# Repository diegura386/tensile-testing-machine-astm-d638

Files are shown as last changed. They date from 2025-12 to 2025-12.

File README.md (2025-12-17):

# tensile-testing-machine-astm-d638
Open-hardware tensile testing machine for plastics (ASTM D638). Project by Diego Víctor Saavedra Ravier.  ➠  [Read this README in English](README.en.md)

# Máquina de Ensayo de Tracción de Plásticos (ASTM D638)



Máquina de ensayo de tracción (UTM) para **plásticos**, orientada a piezas fabricadas por **manufactura aditiva (impresión 3D)** y diseñada para cumplir con los requerimientos de la norma **ASTM D638**, para garantizar obtener ensayos válidos y comparables con otras máquinas bajo el mismo estándar.

Proyecto de **grado en Ingeniería Electromecánica** – UTN FR Chubut.

> Título académico: **Máquina de ensayo de tracción de plásticos** *Diseño y cálculo según norma ASTM D638*

> Autor: **Diego Víctor Saavedra Ravier** 

> Año: **2025**  

> Licencias: **CC BY-SA 4.0** (documentación) y **CERN-OHL-S v2** (hardware)

> Documentación completa del trabajo   ➠   

---

## 📸 Vista general de la máquina

<p align="center">
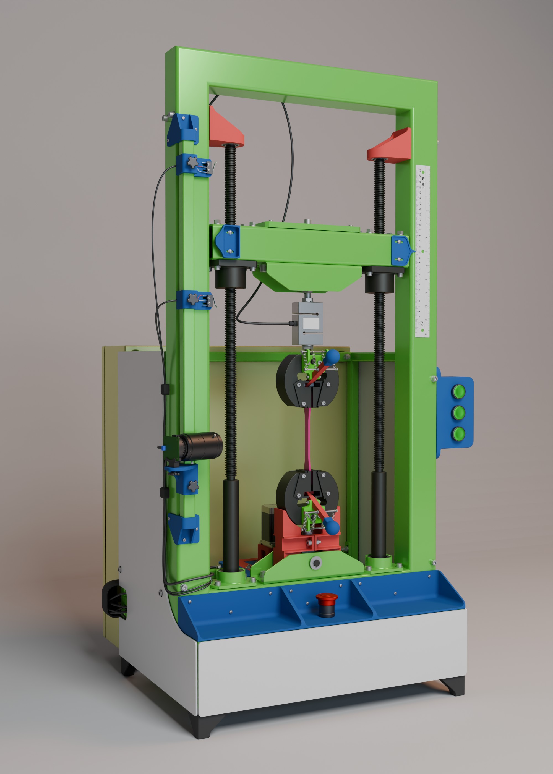
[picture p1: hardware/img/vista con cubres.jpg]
Máquina de Ensayo de Tracción de Plásticos - Render frontal
  
</p>

---

## 🧩 Descripción general

Este proyecto presenta el **diseño y cálculo** de una máquina de ensayo de tracción para todo tipo de plásticos, pero con mayor foco en materiales utilizados en **Manufactura Aditiva** (FFF/FDM, SLA, SLS, etc.). 
La máquina busca ser:

- **Accesible y de bajo costo**
- **Replicable** con recursos locales
- **Documentada y abierta** para la comunidad académica y maker

El diseño cumple con los requerimientos principales de la norma **ASTM D638** (norma empleada para realizar ensayos de tracción de plásticos) para probetas tipo “dog bone”, poniendo especial énfasis en:

- Limitación de la deformación propia de la máquina  
- Correcta selección de celda de carga, transmisión, estructura, mordazas y accesorios  
- Posibilidad de integrar un sistema extensométrico basado en **correlación digital de imágenes (DIC)**

Actualmente el proyecto abarca el diseño completo, cálculos, propuesta de electrónica y control, planos, listado de materiales (BOM) y costos de fabricación. No se incluye la fabricación del prototipo físico.

---

## 🔧 Características principales

- **Norma de referencia:** **ASTM D638** (ensayo de tracción en plásticos)
- **Capacidad de ensayo objetivo:** hasta **10 kN** (dimensionada para cubrir la mayoría de polímeros usados en impresión 3D)
- **Rigidez:** **25,4[kN/mm]** (para cumplir con el requerimiento 5.1.6 de la norma)
- **Peso de la máquina:** **75[kg]**
- **Probetas:** **tipo (I, II, III, IV, V)**
- **Velocidad máxima:** **100[mm/min]**
- **Ámbito de uso:**  
  - Laboratorios de universidades e institutos  
  - Talleres y emprendimientos que utilizan manufactura aditiva
  - Industria del plástico
- **Diseño estructural:**  
  - Marco con caños estructurales
  - Cruceta móvil en la parte superior de la máquina 
  - Sistema de transmisión con tornillos de potencia trapezoidal (TR20x4) y caja reductora con poleas y correas sincrónicas (perfil XL-L)
  - Mordazas del tipo cuñas con palanca y resortes (Wedge Grip)
  - Uso intensivo de análisis FEA en componentes críticos para garantizar un FDS>2 a máxima capacidad de la máquina
- **Componentes impresos en 3D:**  
  - Caja reductora de 2 etapas con poleas y correas sincrónicas (i=8,16 T=11Nm)
  - Piezas auxiliares y de soporte
- **Sistema extensométrico propuesto:**  
  - **DIC** con Raspberry Pi + cámara de 108 MP Arducam  
  - Alternativas de software open source para el procesado de imágenes

---
### 🔄 Estado del proyecto

- ✅ Diseño y documentación completos
- ⚙️ En espera que alguien se anime a fabricar el prototipo
- 📈 Abierto a mejoras y contribuciones

---
### 🎯 Objetivo del proyecto

- ⚙️ Fabricación del primer prototipo
- ⚙️ Feedback de parte de la comunidad respecto a mejoras o revisiones
- ⚙️ Desarrollar una variante de esta máquina de tracción para realizar otro tipo de ensayos, como **flexión**, **compresión**, o incluso para traccionar madera de acuerdo a norma **ASTM D143**
- 📈 Feedback de parte de la comunidad respecto a mejoras a realizar en la **caja reductora**, para elevar el torque resultante o incluso implementar una 3ra etapa para triplicar el torque hasta más de 30Nm (ver sección 5.2.1 del informe ➠   )
- 🔌 Posibilidad de implementar una integración de software y control de la máquina, dedicado a este proyecto
- 💡 Desarrollar el método de ensayo de tracción sin el uso de un extensómetro (ver sección 6.8 del informe  ➠   )

---
## 📂 Estructura del repositorio

> Nota: Esta sección describe la estructura de los archivos de este proyecto.

```text
tensile-testing-machine-astm-d638/
│
├── hardware/                    # Hardware bajo licencia (CERN-OHL-S v2)          
│   ├── cad/                     # Archivos CAD nativos (ensambles, piezas)       
│   ├── drawings/                # Planos técnicos (PDF, DWG, DXF)          
│   │   ├── mechanical/          # Planos mecánicos de conjuntos y piezas          
│   │   └── electrical/          # Planos eléctricos con esquema de componentes, topográfico y conexionado
│   ├── img/                     # Imágenes y renders de la máquina  
│   ├── step/                    # Exportaciones neutrales (STEP, IGES)          
│   └── stl/                     # Archivos STL para impresión 3D
│
├── LICENSE_CERN_OHL_S           # Licencia para hardware (CERN-OHL-S v2)
└── README.md                    # Este archivo

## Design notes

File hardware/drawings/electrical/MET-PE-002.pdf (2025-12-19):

Alimentación 220VAC (Conector C14 hembra con switch y fusible) 21 | 43 | 43 | 43 | 43 | 43

# CONEXIONADO TABLERO ELECTRICO

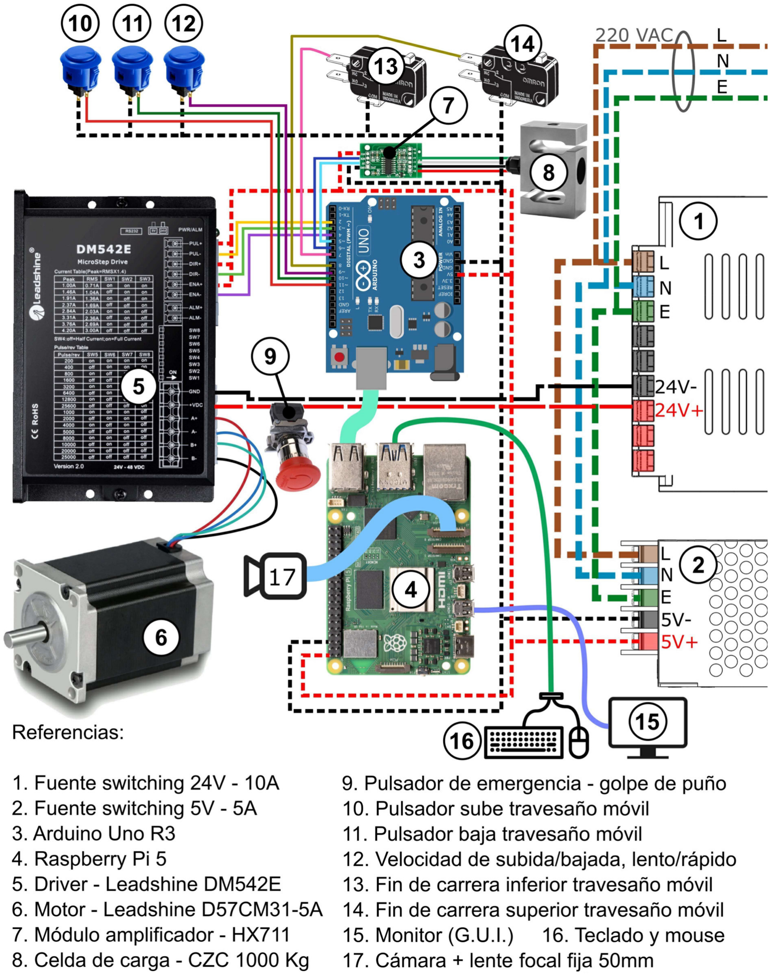
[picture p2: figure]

# UTN

FRCH FACULTAD REGIONAL CHUBUT

## ESQUEMA ELECTRICO

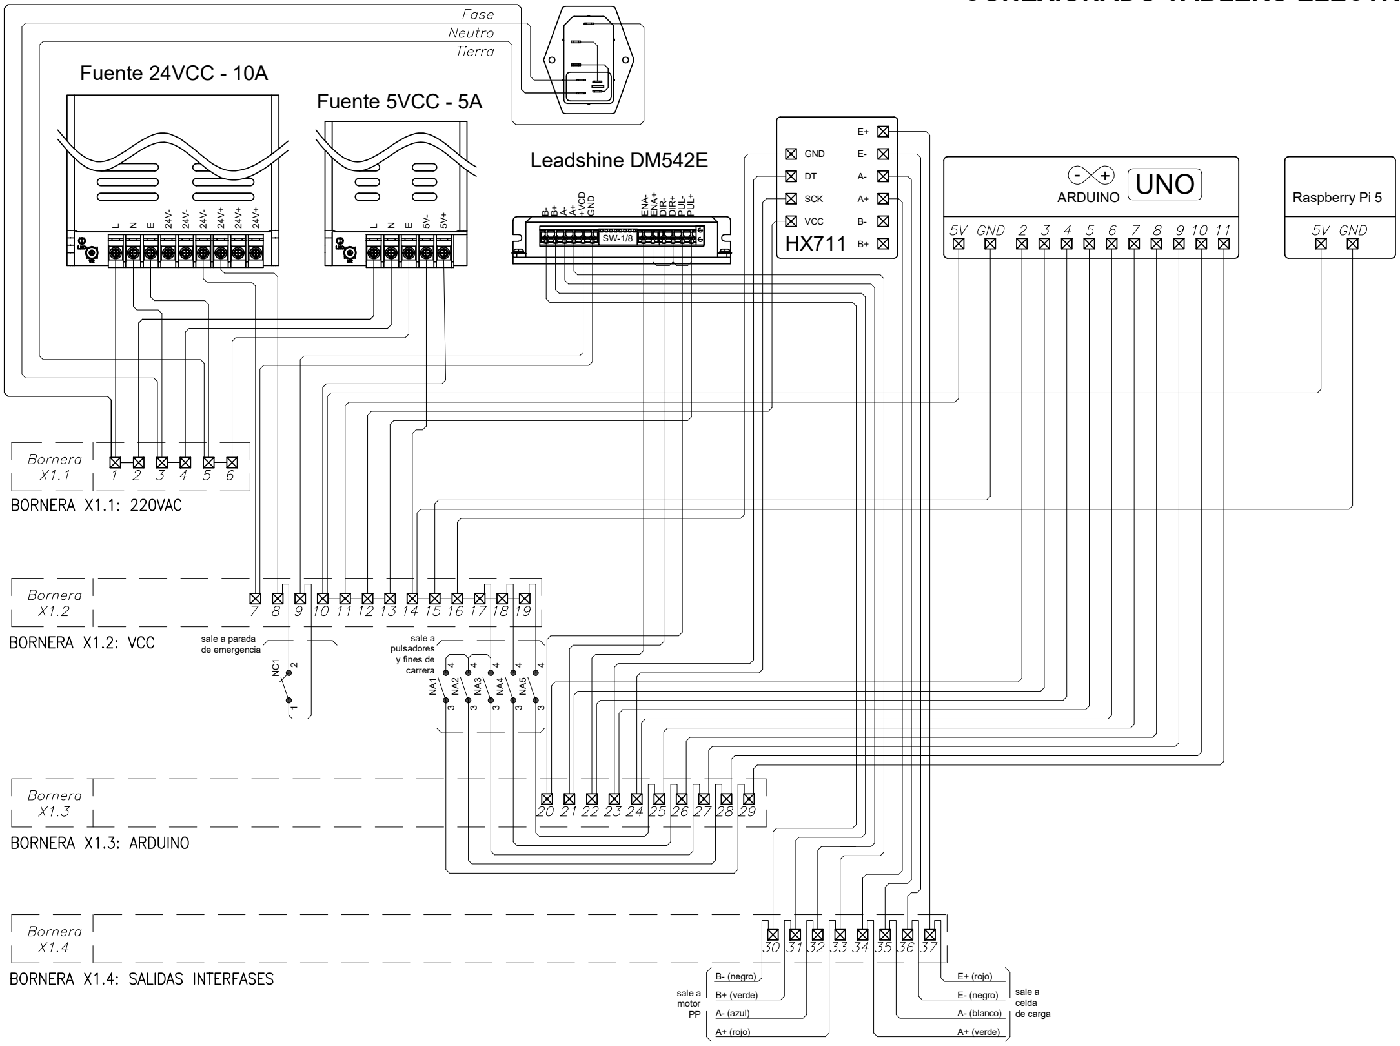
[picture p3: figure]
ARDUINO; UNO; GND; SCK; VCC HX711; Leadshine DM542E; Fuente 5VCC - 5A; Fuente 24VCC - 10A; Raspberry Pi 5; sale a motor PP; A+ (verde); A- (blanco); E- (negro); E+ (rojo); A+ (rojo); A- (azul); B+ (verde); B- (negro); sale a celda de carga; +VCD GND; ENA-; ENA+ DIR-; DIR+ PUL-; PUL+; sale a parada de emergencia; sale a pulsadores y fines de carrera
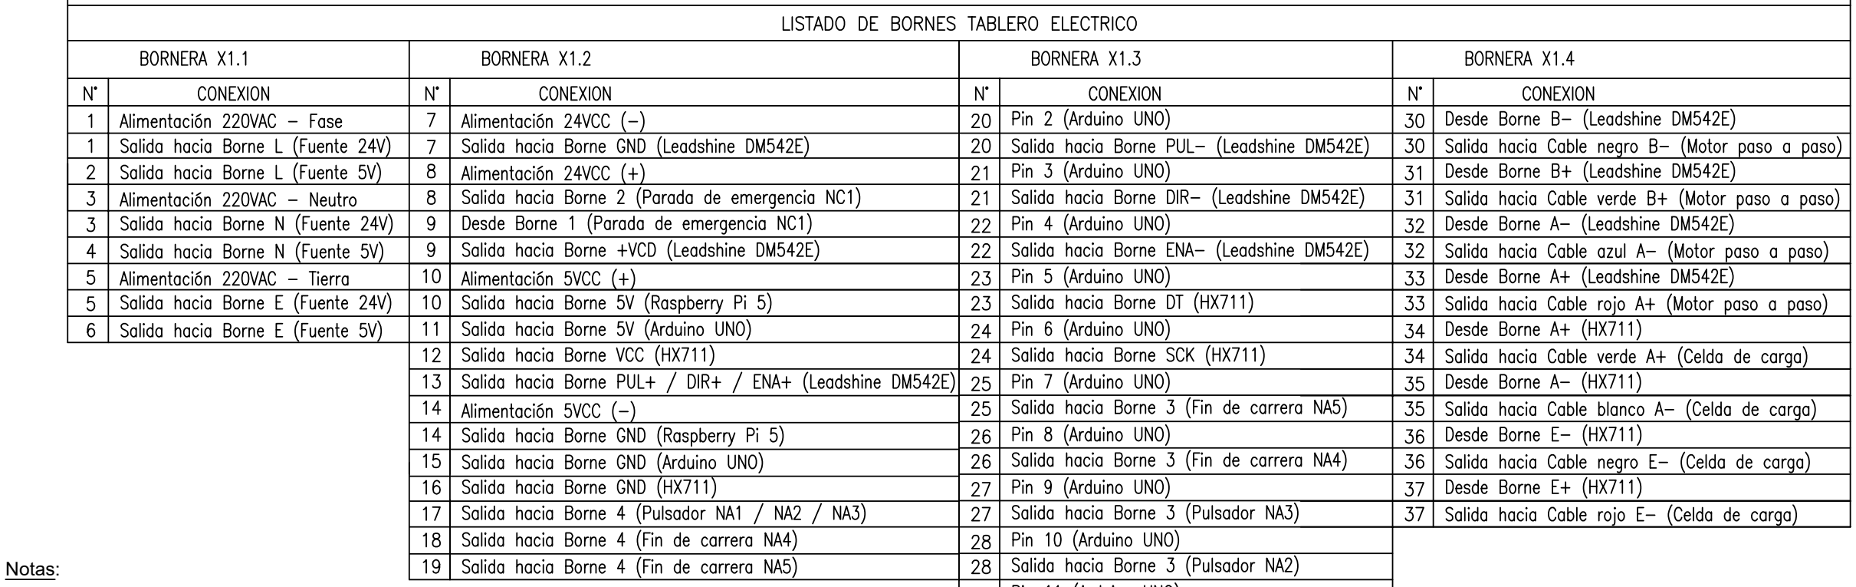
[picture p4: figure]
Notas:

1) Los componentes (6,8,9,10,11,12,13,14,15,16) van fuera del tablero eléctrico.
2) Los componentes deberán contar con refrigeración pasiva y el gabinete eléctrico con una entrada de aire tipo rejilla.
3) En caso de que el Driver [5] presente calentamiento excesivo, instalarle al gabinete eléctrico un ventilador de 24VCC.
4) Del borne 17 al 29 los cables son unipolares (clase 5) de 0,25[mm²] de la marca Kalop.
Para el resto de los bornes los cables son unipolares (clase 5) de 1[mm²] de la marca Kalop.
5) Para más información respecto la disposición de los componentes eléctricos, el gabinete y el ruteo de cables ver el plano MET-PE-001.

tablero
eléctrico
botonera (10-11-12)

14

13

17

9

8

6

COMPONENTES ELECTRICOS EN LA MAQUINA

© 2025 Diego Víctor Saavedra Ravier — Licenciado bajo CERN-OHL-S-2.0 (Strongly Reciprocal). Véase hp://cern.ch/cern-ohl

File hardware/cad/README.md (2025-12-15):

# ⚙️ Archivos CAD y Modelos 3D (SolidWorks & Blender)

Este directorio contiene recursos CAD y modelos 3D utilizados en el diseño, visualización y documentación de la *Máquina de Ensayo de Tracción ASTM D638*.  
Dado que algunos archivos exceden los límites de GitHub, los paquetes completos se distribuyen mediante Zenodo.

---

## 📦 Ensamble completo en SolidWorks (Pack and Go)

El ensamble CAD técnico, utilizado como base del diseño mecánico, está disponible en Zenodo:

🔗 **DOI (SolidWorks):** ➠ 

Este paquete incluye:

- Ensamble principal (`.SLDASM`)
- Piezas individuales (`.SLDPRT`)
- Subensambles completos
- Componentes de Toolbox
- Estructura íntegra generada mediante *Pack and Go*

> ⚠️ **Nota:** Este es el modelo CAD técnico que representa la geometría real utilizada para cálculos, diseño estructural, selección de componentes y generación de planos.

---

## 🎨 Paquete Blender para renders y visualización

El proyecto Blender utilizado para generar renders, animaciones y material visual complementario, se encuentra disponible en Zenodo:

🔗 **DOI (Blender):** ➠  

Este paquete contiene:

- Archivo `.blend` con la escena completa
- Materiales y texturas
- Configuración de luces y cámaras
- Colecciones organizadas para renderizado
- Recursos visuales auxiliares

> 📝 **Este archivo no reemplaza el modelo CAD técnico**, sino que ofrece una representación visual más amigable para documentación, presentaciones y divulgación.

### 🖼️ Imágenes generadas en Blender

<p align="center">
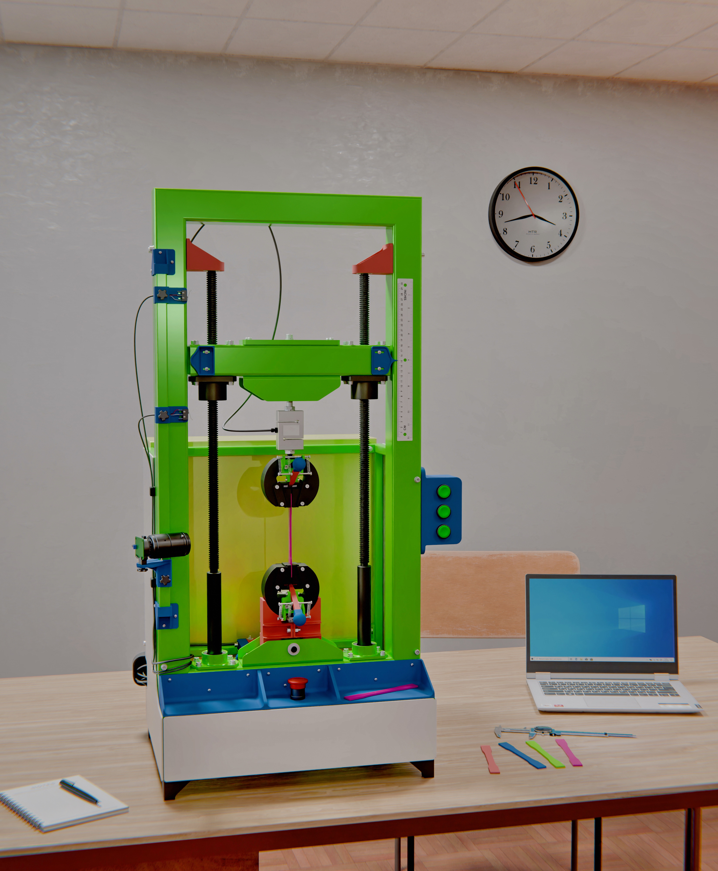
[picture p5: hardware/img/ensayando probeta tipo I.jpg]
  
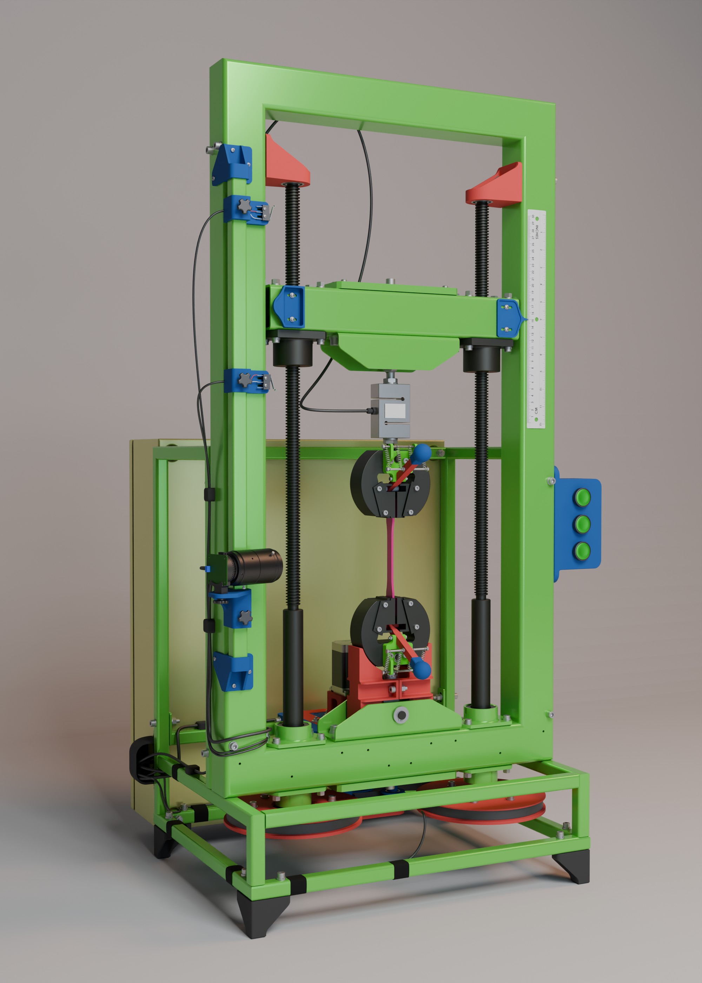
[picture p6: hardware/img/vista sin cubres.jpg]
  
</p>

> 📝 Estas imágenes fueron generadas en Blender y muestran vistas representativas del diseño mecánico y del proceso de ensayo.

---

## 📁 Contenido de este directorio

Este directorio puede incluir archivos CAD livianos o derivados del modelo principal, tales como:

- Archivos CAD individuales (cuando no exceden el límite de GitHub)
- Piezas simplificadas
- Recursos auxiliares para referencia rápida
- Ensamble completo de la máquina para visualizar con eDrawings (`.easm`)

Para abrir el diseño completo o generar renders avanzados, descargar los paquetes correspondientes desde los DOIs indicados arriba.

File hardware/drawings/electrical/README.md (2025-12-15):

# 📐 Planos eléctricos de la máquina

---

## ⚡ Planos

| Nº | ID Plano     | Nombre Pieza                                  |  Formato |
|---:|--------------|-----------------------------------------------|---------|
| 1  | MET-PE-001  | Componentes eléctricos - Topográfico y cableados| A2      |
| 2  | MET-PE-002  | Conexionado eléctrico - Esquema eléctrico       |  A2      |

---

## 📄 Notas

- Todos los planos están licenciados bajo **CERN–OHL–S v2 (Strongly Reciprocal)**.  
- Para los modelos CAD completos, consultar el directorio `/hardware/cad/` y los enlaces DOI asociados.

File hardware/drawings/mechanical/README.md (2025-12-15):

# 📐 Planos Mecánicos – Índice Completo

Este directorio contiene los planos mecánicos de la *Máquina de Ensayo de Tracción para Plásticos según ASTM D638*, correspondientes al **Anexo F – Índice de Planos** del Proyecto Final de Grado.  
A continuación se presenta el **índice oficial de planos**, incluyendo planos de conjuntos y planos de piezas.

---

## 🧩 Planos de Ensamble / Conjuntos

| Nº | ID Plano     | Nombre Conjunto                           | Formato |
|---:|--------------|---------------------------------------------|---------|
| 1  | MET-PME-01   | Ensamble completo de la máquina            | A1      |
| 2  | MET-PMC-100  | Conjunto travesaño fijo                    | A2      |
| 3  | MET-PMC-200  | Conjunto travesaño móvil                   | A2      |
| 4  | MET-PMC-300  | Conjunto mordaza                           | A2      |
| 5  | MET-PMC-400  | Conjunto caja reductora                    | A2      |
| 6  | MET-PMC-500  | Conjunto estructura soporte                | A2      |
| 7  | MET-PMC-600  | Conjunto riel porta fines de carrera       | A2      |
| 8  | MET-PMC-800  | Conjuntos cubres y protectores             | A2      |

---

## 🔩 Planos de Piezas

| Nº | ID Plano     | Nombre Pieza                                  | Conjunto         | Manufactura                          | Peso (g) | Cant. | Total (g) | Formato |
|---:|--------------|-----------------------------------------------|------------------|---------------------------------------|----------:|-------:|-----------:|---------|
| 1  | MET-PMP-001  | Codo salida de cables                         | MET-PME-01       | Manufactura aditiva                   | 38       | 1     | 38        | A3      |
| 2  | MET-PMP-002  | Botonera de control                           | MET-PME-01       | Manufactura aditiva                   | 159      | 1     | 159       | A3      |
| 3  | MET-PMP-003  | Tapa botonera de control                      | MET-PME-01       | Manufactura aditiva                   | 51       | 1     | 51        | A4      |
| 4  | MET-PMP-004  | Asiento de mordaza inferior                   | MET-PME-01       | Manufactura aditiva                   | 85       | 2     | 170       | A3      |
| 5  | MET-PMP-005  | Sujeta caja reductora a riel                  | MET-PME-01       | Manufactura aditiva                   | 191      | 2     | 382       | A3      |
| 6  | MET-PMP-006  | Probeta de prueba                             | MET-PME-01       | Mecanizado                            | 1990     | 1     | 1990      | A4      |
| 7  | MET-PMP-007  | Probeta sujeta celda patrón                    | MET-PME-01       | Mecanizado                            | 634      | 2     | 1268      | A4      |
| 8  | MET-PMP-101  | Marco chasis                                  | MET-PMC-100      | Calderería liviana                    | 15151    | 1     | 15151     | A1      |
| 9  | MET-PMP-102  | Horquilla inferior                            | MET-PMC-100      | Mecanizado + calderería liviana       | 1040     | 1     | 1040      | A2      |
| 10 | MET-PMP-103  | Placa de sujeción                             | MET-PMC-100/200  | Calderería liviana                    | 793      | 2     | 1586      | A3      |
| 11 | MET-PMP-104  | Pasador rótula inferior                       | MET-PMC-100      | Mecanizado                            | 70       | 1     | 70        | A4      |
| 12 | MET-PMP-105  | Portarodamiento 30203                         | MET-PMC-100      | Mecanizado                            | 258      | 4     | 1032      | A3      |
| 13 | MET-PMP-106  | Buje separador rodamiento 30203               | MET-PMC-100      | Mecanizado                            | 18       | 2     | 36        | A4      |
| 14 | MET-PMP-107  | Tornillo TR20x4                               | MET-PMC-100      | Mecanizado                            | 2180     | 2     | 4360      | A3      |
| 15 | MET-PMP-108  | Portarodamiento 6002                          | MET-PMC-100      | Manufactura aditiva                   | 77       | 2     | 154       | A3      |
| 16 | MET-PMP-109  | Brida polea eje tornillo                      | MET-PMC-100      | Mecanizado                            | 611      | 2     | 1222      | A3      |
| 17 | MET-PMP-110  | Polea Z6 L60                                   | MET-PMC-100      | Manufactura aditiva                   | 516      | 2     | 1032      | A3      |
| 18 | MET-PMP-201  | Cruceta móvil                                 | MET-PMC-200      | Calderería liviana                    | 2068     | 1     | 2068      | A3      |
| 19 | MET-PMP-202  | Horquilla superior                            | MET-PMC-200      | Mecanizado + calderería liviana       | 1028     | 1     | 1028      | A2      |
| 20 | MET-PMP-203  | Pasador rótula superior                       | MET-PMC-200      | Mecanizado                            | 37       | 1     | 37        | A4      |
| 21 | MET-PMP-204  | Brida porta tuerca                            | MET-PMC-200      | Mecanizado                            | 519      | 2     | 1038      | A3      |
| 22 | MET-PMP-205  | Tuerca TR20                                    | MET-PMC-200      | Mecanizado                            | 427      | 2     | 854       | A3      |
| 23 | MET-PMP-206  | Leva fin de carrera                           | MET-PMC-200      | Manufactura aditiva                   | 11       | 1     | 11        | A4      |
| 24 | MET-PMP-207  | Aguja desplazamiento cruceta móvil            | MET-PMC-200      | Manufactura aditiva                   | 6        | 1     | 6         | A4      |
| 25 | MET-PMP-301  | Cuerpo mordaza                                | MET-PMC-300      | Mecanizado                            | 1648     | 2     | 3296      | A3      |
| 26 | MET-PMP-302  | Perno de sujeción mordaza                     | MET-PMC-300      | Mecanizado                            | 56       | 2     | 112       | A4      |
| 27 | MET-PMP-303  | Pivote tensor                                 | MET-PMC-300      | Manufactura aditiva                   | 13       | 2     | 26        | A3      |
| 28 | MET-PMP-304  | Pasador mordaza                               | MET-PMC-300      | Mecanizado                            | 19       | 2     | 38        | A4      |
| 29 | MET-PMP-305  | Cuña mordaza                                  | MET-PMC-300      | Mecanizado                            | 212      | 4     | 848       | A3      |
| 30 | MET-PMP-306  | Guía cuña                                     | MET-PMC-300      | Mecanizado                            | 18       | 8     | 144       | A4      |
| 31 | MET-PMP-307  | Brazo sujeción cuñas                          | MET-PMC-300      | Manufactura aditiva                   | 12       | 2     | 24        | A3      |
| 32 | MET-PMP-308  | Mango brazo                                   | MET-PMC-300      | Manufactura aditiva                   | 7        | 2     | 14        | A3      |
| 33 | MET-PMP-309  | Rodillo leva cuña                             | MET-PMC-300      | Manufactura aditiva                   | 1        | 4     | 4         | A4      |
| 34 | MET-PMP-401  | Cuerpo caja reductora                         | MET-PMC-400      | Manufactura aditiva                   | 340      | 1     | 340       | A2      |
| 35 | MET-PMP-402  | Tapa caja reductora                           | MET-PMC-400      | Manufactura aditiva                   | 207      | 1     | 207       | A3      |
| 36 | MET-PMP-403  | Tapa rodamiento 61810                         | MET-PMC-400      | Manufactura aditiva                   | 50       | 1     | 50        | A3      |
| 37 | MET-PMP-404  | Soporte motor                                 | MET-PMC-400      | Manufactura aditiva                   | 95       | 1     | 95        | A3      |
| 38 | MET-PMP-405  | Eje mando caja                                | MET-PMC-400      | Mecanizado                            | 38       | 1     | 38        | A4      |
| 39 | MET-PMP-406  | Eje tensor caja                               | MET-PMC-400      | Mecanizado                            | 29       | 1     | 29        | A4      |
| 40 | MET-PMP-407  | Polea Z1 XL14 075                             | MET-PMC-400      | Manufactura aditiva                   | 10       | 1     | 10        | A3      |
| 41 | MET-PMP-408  | Polea Z2-Z3 XL40 037 / XL14 075               | MET-PMC-400      | Manufactura aditiva                   | 70       | 1     | 70        | A3      |
| 42 | MET-PMP-409  | Polea Z4 XL40 075                             | MET-PMC-400      | Manufactura aditiva                   | 114      | 1     | 114       | A3      |
| 43 | MET-PMP-410  | Poleas Z5 L18 050                             | MET-PMC-400      | Manufactura aditiva                   | 126      | 1     | 126       | A3      |
| 44 | MET-PMP-411  | Acople flexible TPU                           | MET-PMC-400      | Manufactura aditiva                   | 1        | 4     | 4         | A4      |
| 45 | MET-PMP-412  | Tensor Z2-Z3                                  | MET-PMC-400      | Manufactura aditiva                   | 26       | 2     | 52        | A3      |
| 46 | MET-PMP-413  | Buje separador Z1-Z3-Z4                       | MET-PMC-400      | Manufactura aditiva                   | 1        | 3     | 3         | A4      |
| 47 | MET-PMP-414  | Buje separador Z2                             | MET-PMC-400      | Manufactura aditiva                   | 1        | 1     | 1         | A4      |
| 48 | MET-PMP-415  | Seguro Seeger eje tensor                      | MET-PMC-400      | Manufactura aditiva                   | 1        | 2     | 2         | A4      |
| 49 | MET-PMP-416  | Tensor Z5-Z6                                  | MET-PMC-400      | Manufactura aditiva                   | 12       | 2     | 24        | A4      |
| 50 | MET-PMP-417  | Buje corto separador tensor                   | MET-PMC-400      | Manufactura aditiva                   | 1        | 2     | 2         | A4      |
| 51 | MET-PMP-418  | Buje largo separador tensor                   | MET-PMC-400      | Manufactura aditiva                   | 3        | 2     | 6         | A4      |
| 52 | MET-PMP-419  | Viga tensores                                 | MET-PMC-400      | Manufactura aditiva                   | 52       | 1     | 52        | A4      |
| 53 | MET-PMP-501  | Estructura soporte                            | MET-PMC-500      | Calderería liviana                    | 6361     | 1     | 6361      | A2      |
| 54 | MET-PMP-502  | Soporte caja reductora                        | MET-PMC-500      | Calderería liviana                    | 1565     | 1     | 1565      | A2      |
| 55 | MET-PMP-503  | Pata máquina                                  | MET-PMC-500      | Manufactura aditiva                   | 44       | 4     | 176       | A3      |
| 56 | MET-PMP-601  | Porta riel                                    | MET-PMC-600      | Manufactura aditiva                   | 25       | 2     | 50        | A3      |
| 57 | MET-PMP-602  | Porta fin de carrera                          | MET-PMC-600      | Manufactura aditiva                   | 26       | 2     | 52        | A3      |
| 58 | MET-PMP-603  | Porta cámara                                  | MET-PMC-600      | Manufactura aditiva                   | 30       | 1     | 30        | A3      |
| 59 | MET-PMP-801  | Panel cubre lateral izquierdo                 | MET-PMC-800      | CNC Láser                             | 56       | 1     | 56        | A3      |
| 60 | MET-PMP-802  | Panel cubre lateral derecho                   | MET-PMC-800      | CNC Láser                             | 58       | 1     | 58        | A3      |
| 61 | MET-PMP-803  | Panel cubre frontal                           | MET-PMC-800      | CNC Láser                             | 18       | 1     | 18        | A3      |
| 62 | MET-PMP-804  | Cubre frente lateral                          | MET-PMC-800      | Manufactura aditiva                   | 155      | 2     | 310       | A3      |
| 63 | MET-PMP-805  | Cubre frente medio                            | MET-PMC-800      | Manufactura aditiva                   | 119      | 1     | 119       | A3      |

---

## 📄 Notas

- El presente índice corresponde íntegramente al **Anexo F – Índice de planos** del Proyecto Final de Grado.  
- Todos los planos están licenciados bajo **CERN–OHL–S v2 (Strongly Reciprocal)**.  
- Para los modelos CAD completos, consultar el directorio `/hardware/cad/` y los enlaces DOI asociados.

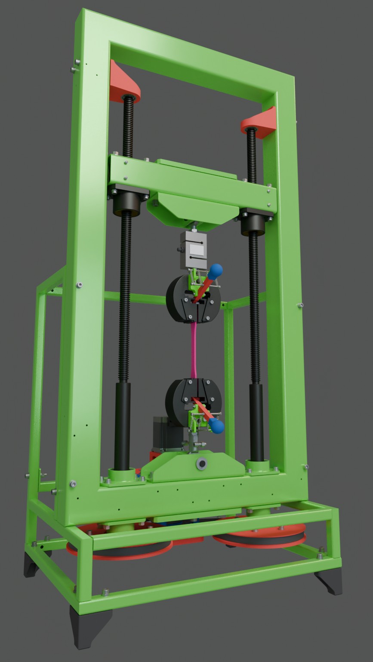
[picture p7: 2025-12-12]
hardware/img/perspectiva.jpg

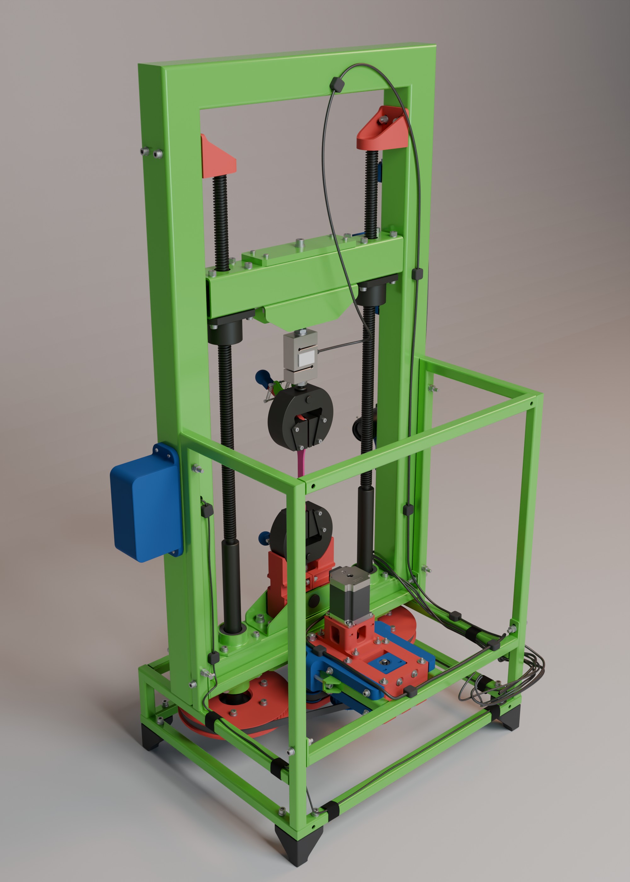
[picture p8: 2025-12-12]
hardware/img/vista sin gabinete electrico ni cubres.jpg

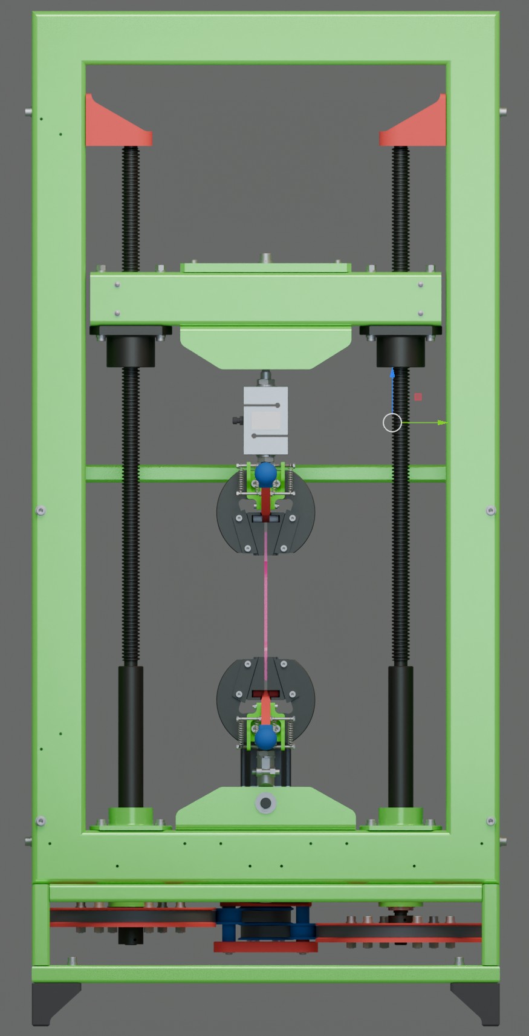
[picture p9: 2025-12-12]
hardware/img/vista frontal.jpg

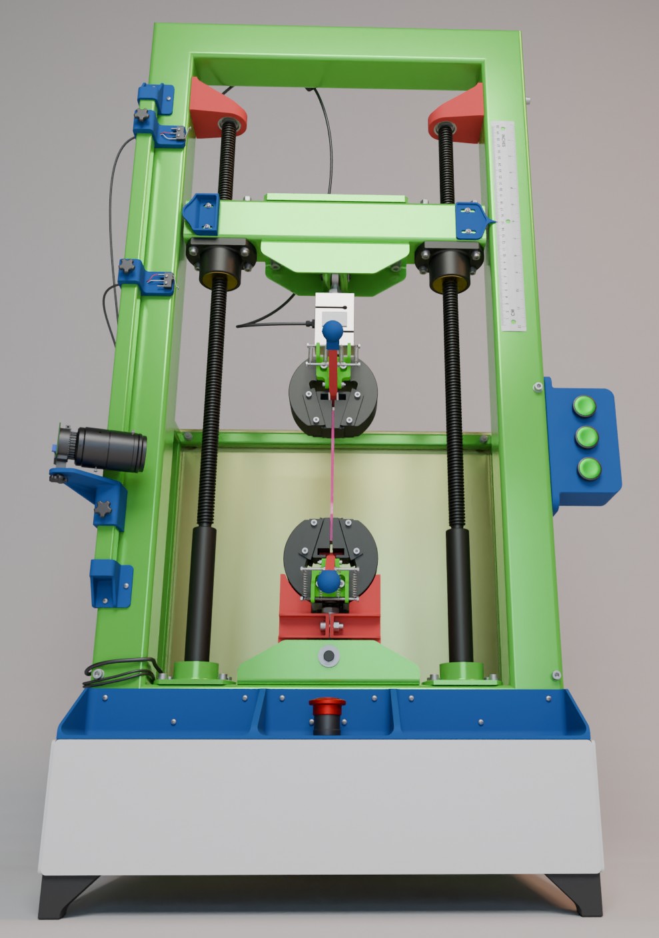
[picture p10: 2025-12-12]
hardware/img/frontal inferior.jpg

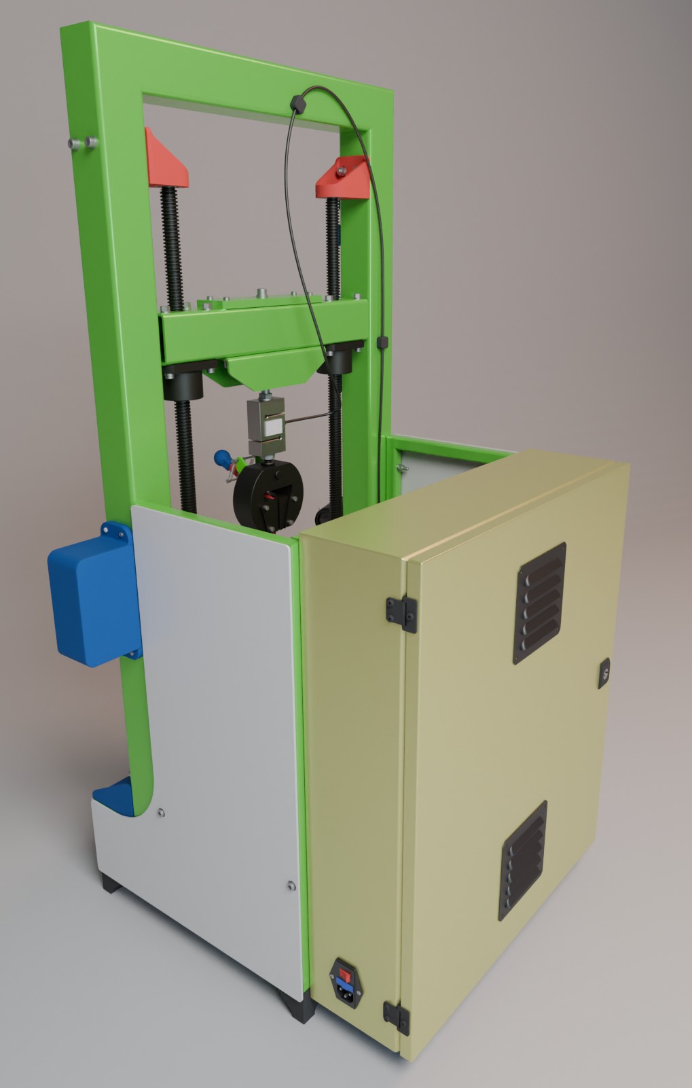
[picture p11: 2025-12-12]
hardware/img/vista trasera.jpg

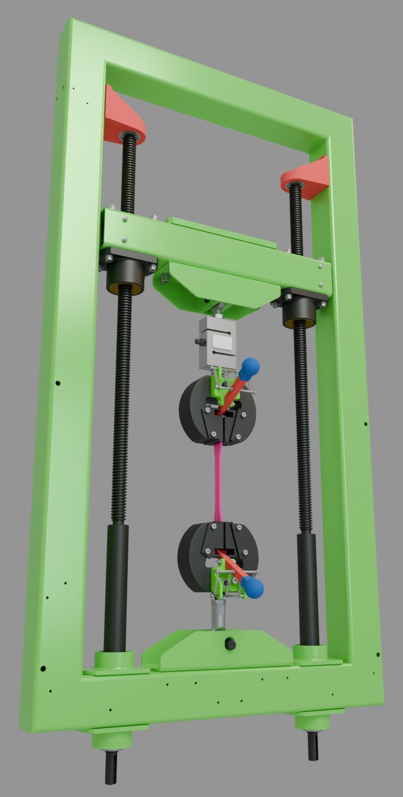
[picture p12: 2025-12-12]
hardware/img/tornillos y mordazas.jpg

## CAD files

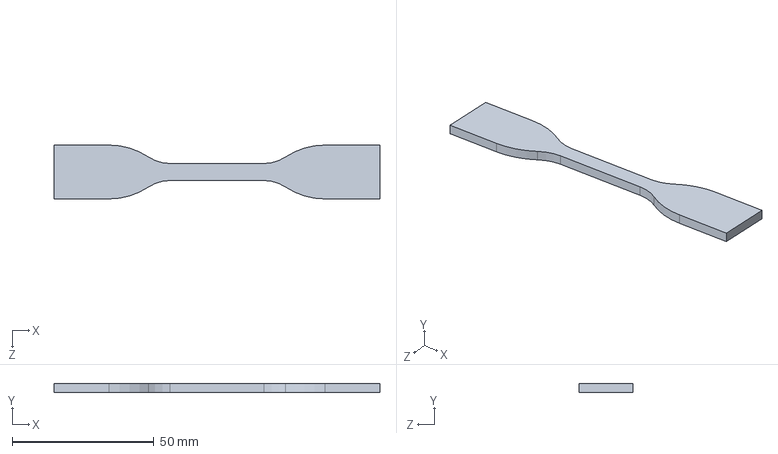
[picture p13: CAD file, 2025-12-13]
hardware/cad/solidworks/Probeta astmD638_Type IV.SLDPRT
115.0 x 3.20 x 19.0 mm

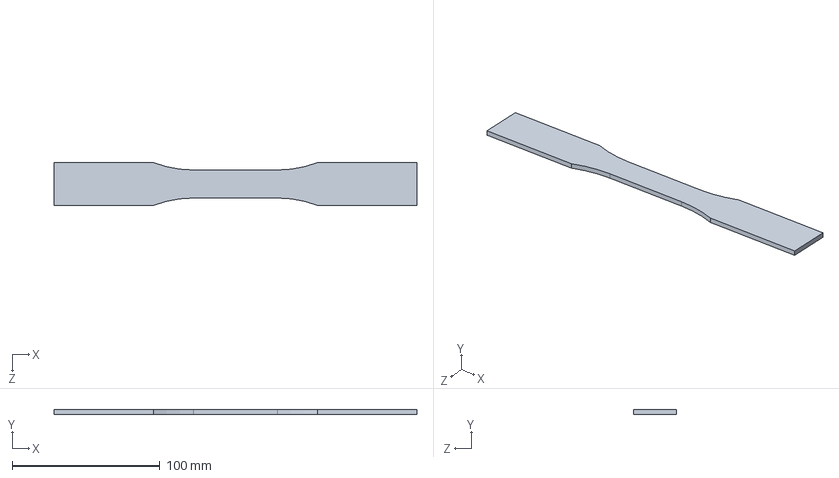
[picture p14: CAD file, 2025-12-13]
hardware/cad/solidworks/Probeta astmD638_Type III.SLDPRT
246.0 x 3.20 x 29.0 mm

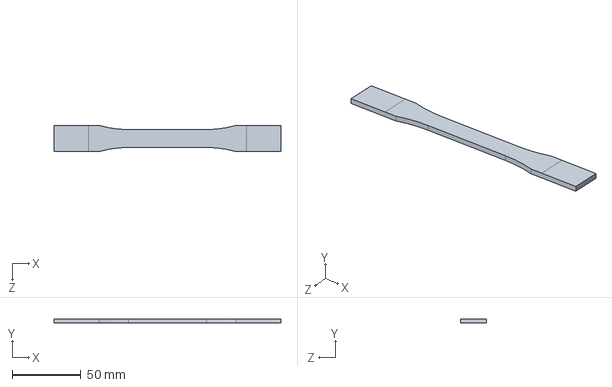
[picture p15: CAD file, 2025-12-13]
hardware/cad/solidworks/Probeta astmD638_Type I.SLDPRT
165.0 x 3.20 x 19.0 mm

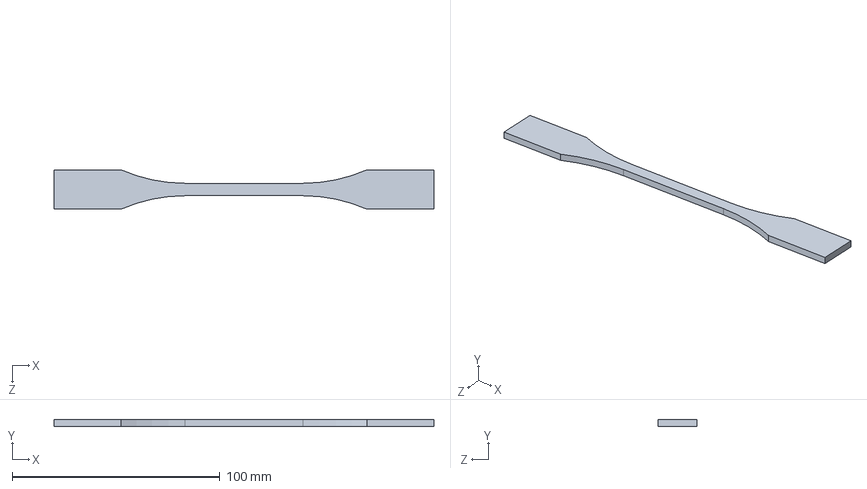
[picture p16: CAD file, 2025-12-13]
hardware/cad/solidworks/Probeta astmD638_Type II.SLDPRT
183.0 x 3.20 x 19.0 mm

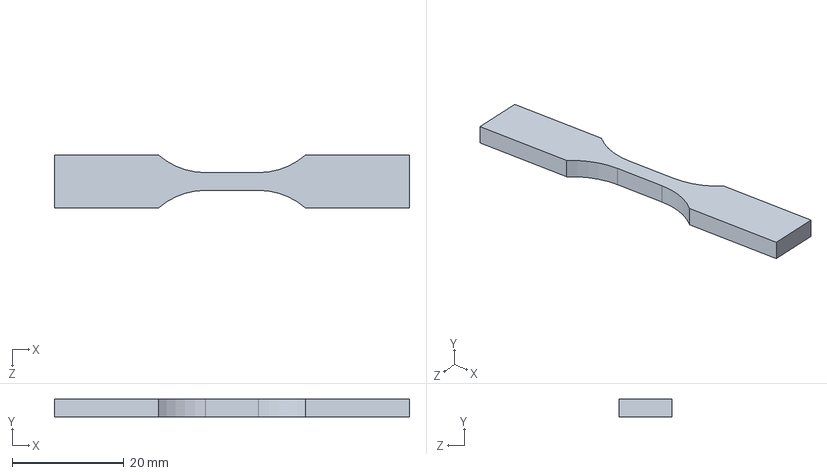
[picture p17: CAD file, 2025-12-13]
hardware/cad/solidworks/Probeta astmD638_Type V.SLDPRT
63.5 x 3.18 x 9.53 mm

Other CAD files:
hardware/stl/Probeta astmD638_Type I.STL
hardware/stl/Probeta astmD638_Type II.STL
hardware/stl/Probeta astmD638_Type III.STL
hardware/stl/Probeta astmD638_Type IV.STL
hardware/stl/Probeta astmD638_Type V.STL

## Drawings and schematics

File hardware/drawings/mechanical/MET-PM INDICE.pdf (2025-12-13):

G G

H H

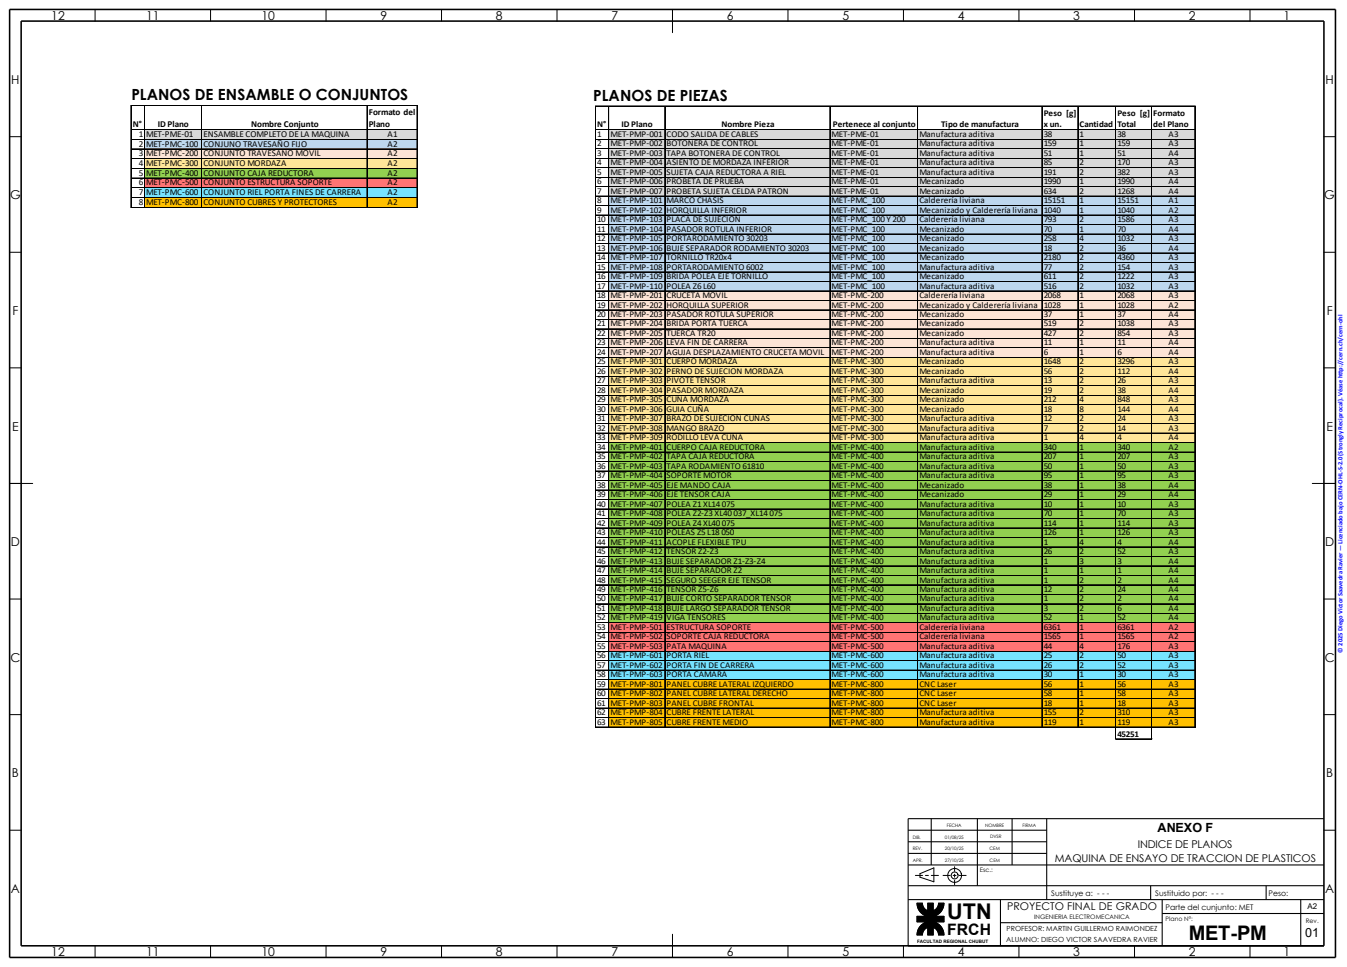
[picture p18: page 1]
UTN; PLANOS DE ENSAMBLE O CONJUNTOS; PLANOS DE PIEZAS; ID Plano; Nombre Conjunto; Formato del Plano; 1 MET-PME-01; ENSAMBLE COMPLETO DE LA MAQUINA; 2 MET-PMC-100; CONJUNO TRAVESAÑO FIJO; 3 MET-PMC-200; CONJUNTO TRAVESAÑO MOVIL; 4 MET-PMC-300; CONJUNTO MORDAZA; 5 MET-PMC-400; CONJUNTO CAJA REDUCTORA; 6 MET-PMC-500; CONJUNTO ESTRUCTURA SOPORTE; 7 MET-PMC-600; CONJUNTO RIEL PORTA FINES DE CARRERA; 8 MET-PMC-800; CONJUNTO CUBRES Y PROTECTORES; Nombre Pieza; Pertenece al conjunto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

9 | MET-PMP-102 | HORQUILLA INFERIOR | MET-PMC_100 | Mecanizado y Calderería liviana | 1040 | 1 | 1040 | A2
10 | MET-PMP-103 | PLACA DE SUJECION | MET-PMC_100 Y 200 | Calderería liviana | 793 | 2 | 1586 | A3
11 | MET-PMP-104 | PASADOR ROTULA INFERIOR | MET-PMC_100 | Mecanizado | 70 | 1 | 70 | A4
12 | MET-PMP-105 | PORTARODAMIENTO 30203 | MET-PMC_100 | Mecanizado | 258 | 4 | 1032 | A3
13 | MET-PMP-106 | BUJE SEPARADOR RODAMIENTO 30203 | MET-PMC_100 | Mecanizado | 18 | 2 | 36 | A4
14 | MET-PMP-107 | TORNILLO TR20x4 | MET-PMC_100 | Mecanizado | 2180 | 2 | 4360 | A3
15 | MET-PMP-108 | PORTARODAMIENTO 6002 | MET-PMC_100 | Manufactura aditiva | 77 | 2 | 154 | A3
16 | MET-PMP-109 | BRIDA POLEA EJE TORNILLO | MET-PMC_100 | Mecanizado | 611 | 2 | 1222 | A3
17 | MET-PMP-110 | POLEA Z6 L60 | MET-PMC_100 | Manufactura aditiva | 516 | 2 | 1032 | A3
18 | MET-PMP-201 | CRUCETA MOVIL | MET-PMC-200 | Calderería liviana | 2068 | 1 | 2068 | A3
20 | MET-PMP-203 | PASADOR ROTULA SUPERIOR | MET-PMC-200 | Mecanizado | 37 | 1 | 37 | A4
21 | MET-PMP-204 | BRIDA PORTA TUERCA | MET-PMC-200 | Mecanizado | 519 | 2 | 1038 | A3
22 | MET-PMP-205 | TUERCA TR20 | MET-PMC-200 | Mecanizado | 427 | 2 | 854 | A3
23 | MET-PMP-206 | LEVA FIN DE CARRERA | MET-PMC-200 | Manufactura aditiva | 11 | 1 | 11 | A4
24 | MET-PMP-207 | AGUJA DESPLAZAMIENTO CRUCETA MOVIL | MET-PMC-200 | Manufactura aditiva | 6 | 1 | 6 | A4
25 | MET-PMP-301 | CUERPO MORDAZA | MET-PMC-300 | Mecanizado | 1648 | 2 | 3296 | A3
26 | MET-PMP-302 | PERNO DE SUJECION MORDAZA | MET-PMC-300 | Mecanizado | 56 | 2 | 112 | A4
27 | MET-PMP-303 | PIVOTE TENSOR | MET-PMC-300 | Manufactura aditiva | 13 | 2 | 26 | A3
28 | MET-PMP-304 | PASADOR MORDAZA | MET-PMC-300 | Mecanizado | 19 | 2 | 38 | A4
29 | MET-PMP-305 | CUÑA MORDAZA | MET-PMC-300 | Mecanizado | 212 | 4 | 848 | A3
30 | MET-PMP-306 | GUIA CUÑA | MET-PMC-300 | Mecanizado | 18 | 8 | 144 | A4
32 | MET-PMP-308 | MANGO BRAZO | MET-PMC-300 | Manufactura aditiva | 7 | 2 | 14 | A3
33 | MET-PMP-309 | RODILLO LEVA CUÑA | MET-PMC-300 | Manufactura aditiva | 1 | 4 | 4 | A4
34 | MET-PMP-401 | CUERPO CAJA REDUCTORA | MET-PMC-400 | Manufactura aditiva | 340 | 1 | 340 | A2
35 | MET-PMP-402 | TAPA CAJA REDUCTORA | MET-PMC-400 | Manufactura aditiva | 207 | 1 | 207 | A3
36 | MET-PMP-403 | TAPA RODAMIENTO 61810 | MET-PMC-400 | Manufactura aditiva | 50 | 1 | 50 | A3
37 | MET-PMP-404 | SOPORTE MOTOR | MET-PMC-400 | Manufactura aditiva | 95 | 1 | 95 | A3
38 | MET-PMP-405 | EJE MANDO CAJA | MET-PMC-400 | Mecanizado | 38 | 1 | 38 | A4
39 | MET-PMP-406 | EJE TENSOR CAJA | MET-PMC-400 | Mecanizado | 29 | 1 | 29 | A4
40 | MET-PMP-407 | POLEA Z1 XL14 075 | MET-PMC-400 | Manufactura aditiva | 10 | 1 | 10 | A3
41 | MET-PMP-408 | POLEA Z2-Z3 XL40 037_XL14 075 | MET-PMC-400 | Manufactura aditiva | 70 | 1 | 70 | A3
42 | MET-PMP-409 | POLEA Z4 XL40 075 | MET-PMC-400 | Manufactura aditiva | 114 | 1 | 114 | A3
43 | MET-PMP-410 | POLEAS Z5 L18 050 | MET-PMC-400 | Manufactura aditiva | 126 | 1 | 126 | A3
45 | MET-PMP-412 | TENSOR Z2-Z3 | MET-PMC-400 | Manufactura aditiva | 26 | 2 | 52 | A3
46 | MET-PMP-413 | BUJE SEPARADOR Z1-Z3-Z4 | MET-PMC-400 | Manufactura aditiva | 1 | 3 | 3 | A4
47 | MET-PMP-414 | BUJE SEPARADOR Z2 | MET-PMC-400 | Manufactura aditiva | 1 | 1 | 1 | A4
48 | MET-PMP-415 | SEGURO SEEGER EJE TENSOR | MET-PMC-400 | Manufactura aditiva | 1 | 2 | 2 | A4
49 | MET-PMP-416 | TENSOR Z5-Z6 | MET-PMC-400 | Manufactura aditiva | 12 | 2 | 24 | A4
50 | MET-PMP-417 | BUJE CORTO SEPARADOR TENSOR | MET-PMC-400 | Manufactura aditiva | 1 | 2 | 2 | A4
51 | MET-PMP-418 | BUJE LARGO SEPARADOR TENSOR | MET-PMC-400 | Manufactura aditiva | 3 | 2 | 6 | A4
52 | MET-PMP-419 | VIGA TENSORES | MET-PMC-400 | Manufactura aditiva | 52 | 1 | 52 | A4
53 | MET-PMP-501 | ESTRUCTURA SOPORTE | MET-PMC-500 | Calderería liviana | 6361 | 1 | 6361 | A2
54 | MET-PMP-502 | SOPORTE CAJA REDUCTORA | MET-PMC-500 | Calderería liviana | 1565 | 1 | 1565 | A2
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

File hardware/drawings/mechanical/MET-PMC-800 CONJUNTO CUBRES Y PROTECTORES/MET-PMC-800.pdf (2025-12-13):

G G

H H

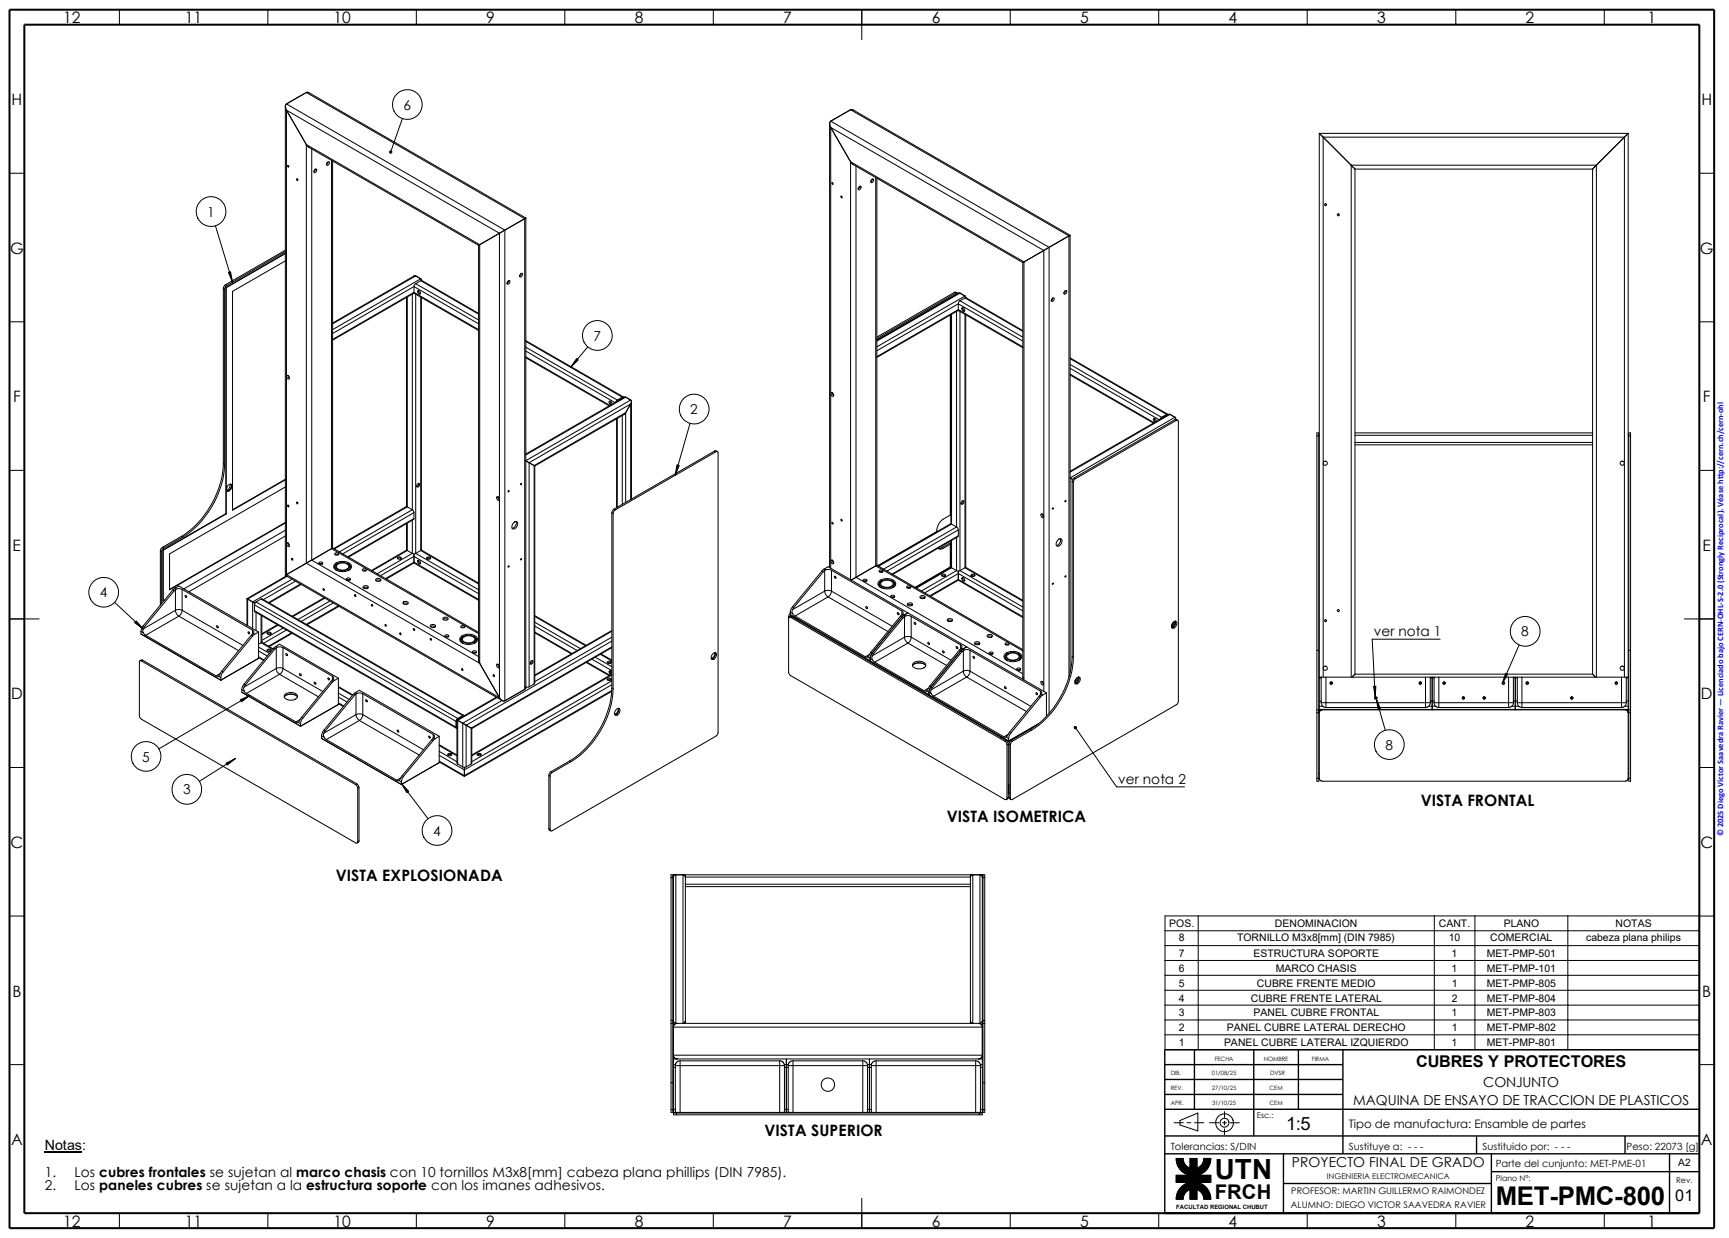
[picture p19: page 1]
UTN; VISTA FRONTAL; ver nota 1; VISTA EXPLOSIONADA; ver nota 2; VISTA ISOMETRICA; VISTA SUPERIOR

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

POS. | DENOMINACION | CANT. | PLANO | NOTAS
8 | TORNILLO M3x8[mm] (DIN 7985) | 10 | COMERCIAL | cabeza plana philips
7 | ESTRUCTURA SOPORTE | 1 | MET-PMP-501
6 | MARCO CHASIS | 1 | MET-PMP-101
5 | CUBRE FRENTE MEDIO | 1 | MET-PMP-805
4 | CUBRE FRENTE LATERAL | 2 | MET-PMP-804
3 | PANEL CUBRE FRONTAL | 1 | MET-PMP-803
2 | PANEL CUBRE LATERAL DERECHO | 1 | MET-PMP-802
1 | PANEL CUBRE LATERAL IZQUIERDO | 1 | MET-PMP-801

FECHA | NOMBRE | FIRMA | CUBRES Y PROTECTORES CONJUNTO MAQUINA DE ENSAYO DE TRACCION DE PLASTICOS

DIB. | 01/08/25 | DVSR

REV. | 27/10/25 | CEM

APR. | 31/10/25 | CEM

Esc.: 1:5 | Tipo de manufactura: Ensamble de partes

Notas:
1. Los cubres frontales se sujetan al marco chasis con 10 tornillos M3x8[mm] cabeza plana phillips (DIN 7985).
2. Los paneles cubres se sujetan a la estructura soporte con los imanes adhesivos.

Tolerancias: S/DIN | Sustituye a: - - - | Sustituido por: - - - | Peso: 22073 [g]

PROYECTO FINAL DE GRADO INGENIERIA ELECTROMECANICA | Parte del cunjunto: MET-PME-01 | A2

FRCH FACULTAD REGIONAL CHUBUT

Plano N°: MET-PMC-800 | Rev. 01

PROFESOR: MARTIN GUILLERMO RAIMONDEZ
ALUMNO: DIEGO VICTOR SAAVEDRA RAVIER

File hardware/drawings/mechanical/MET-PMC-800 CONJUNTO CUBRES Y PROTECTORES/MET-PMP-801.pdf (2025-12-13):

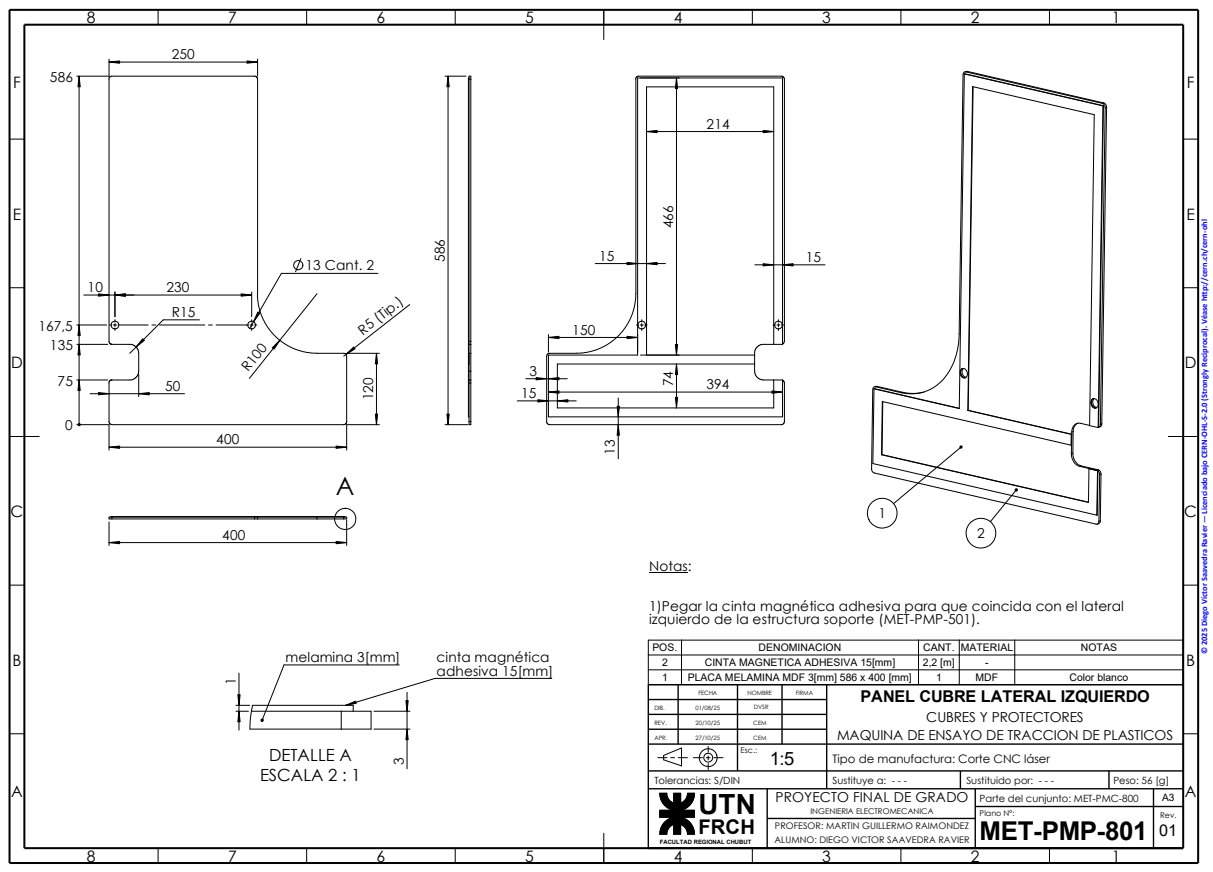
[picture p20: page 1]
UTN FRCH; Notas:; 13 Cant. 2; R5 (Tip.); DETALLE A; melamina 3[mm]; ESCALA 2 : 1; cinta magnética; adhesiva 15[mm] 3 1; © ²⁰²⁵ Diego Víctor Saavedra Ravier — Licenciado bajo CERN⁻OHL⁻S⁻2.0 ⁽Strongly Reciprocal). Véase hp://cern.ch/cern⁻ohl

1)Pegar la cinta magnética adhesiva para que coincida con el lateral
izquierdo de la estructura soporte (MET-PMP-501).

POS. | DENOMINACION | CANT. | MATERIAL | NOTAS
2 | CINTA MAGNETICA ADHESIVA 15[mm] | 2,2 [m] | -
1 | PLACA MELAMINA MDF 3[mm] 586 x 400 [mm] | 1 | MDF | Color blanco
FECHA | | FIRMA NOMBRE | PANEL CUBRE LATERAL IZQUIERDO CUBRES Y PROTECTORES MAQUINA DE ENSAYO DE TRACCION DE PLASTICOS

DIB. | 01/08/25 | DVSR

REV. | 20/10/25 | CEM

APR. | 27/10/25 | CEM

Esc.: 1:5 | Tipo de manufactura: Corte CNC láser

Tolerancias: S/DIN | Sustituye a: - - - | Sustituido por: - - - | Peso: 56 [g]
FACULTAD REGIONAL CHUBUT | | | PROYECTO FINAL DE GRADO INGENIERIA ELECTROMECANICA | Parte del cunjunto: MET-PMC-800 | A3

Plano N°: MET-PMP-801 | Rev. 01

PROFESOR: MARTIN GUILLERMO RAIMONDEZ
ALUMNO: DIEGO VICTOR SAAVEDRA RAVIER

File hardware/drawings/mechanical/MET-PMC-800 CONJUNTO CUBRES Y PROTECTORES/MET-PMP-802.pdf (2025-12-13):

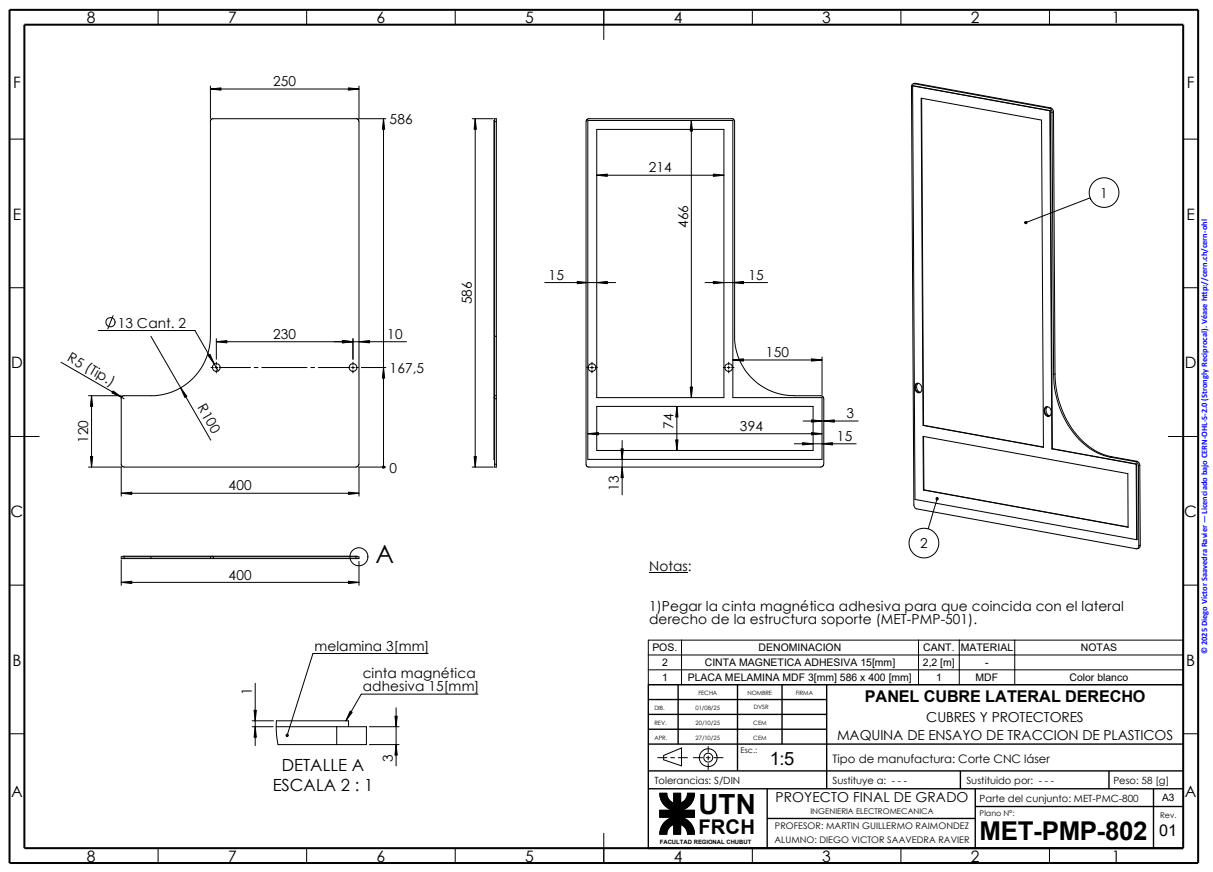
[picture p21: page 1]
UTN FRCH; Notas:; 10 120 R5 (Tip.); 13 Cant. 2; DETALLE A ESCALA 2 : 1; melamina 3[mm]; cinta magnética; adhesiva 15[mm] 3 1

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

1)Pegar la cinta magnética adhesiva para que coincida con el lateral
derecho de la estructura soporte (MET-PMP-501).

POS. | DENOMINACION | CANT. | MATERIAL | NOTAS
2 | CINTA MAGNETICA ADHESIVA 15[mm] | 2,2 [m] | -
1 | PLACA MELAMINA MDF 3[mm] 586 x 400 [mm] | 1 | MDF | Color blanco
FECHA | | FIRMA NOMBRE | PANEL CUBRE LATERAL DERECHO CUBRES Y PROTECTORES MAQUINA DE ENSAYO DE TRACCION DE PLASTICOS

DIB. | 01/08/25 | DVSR

REV. | 20/10/25 | CEM

APR. | 27/10/25 | CEM

Esc.: 1:5 | Tipo de manufactura: Corte CNC láser

Tolerancias: S/DIN | Sustituye a: - - - | Sustituido por: - - - | Peso: 58 [g]

FACULTAD REGIONAL CHUBUT | | | PROYECTO FINAL DE GRADO INGENIERIA ELECTROMECANICA | Parte del cunjunto: MET-PMC-800 | A3

Plano N°: MET-PMP-802 | Rev. 01

PROFESOR: MARTIN GUILLERMO RAIMONDEZ
ALUMNO: DIEGO VICTOR SAAVEDRA RAVIER

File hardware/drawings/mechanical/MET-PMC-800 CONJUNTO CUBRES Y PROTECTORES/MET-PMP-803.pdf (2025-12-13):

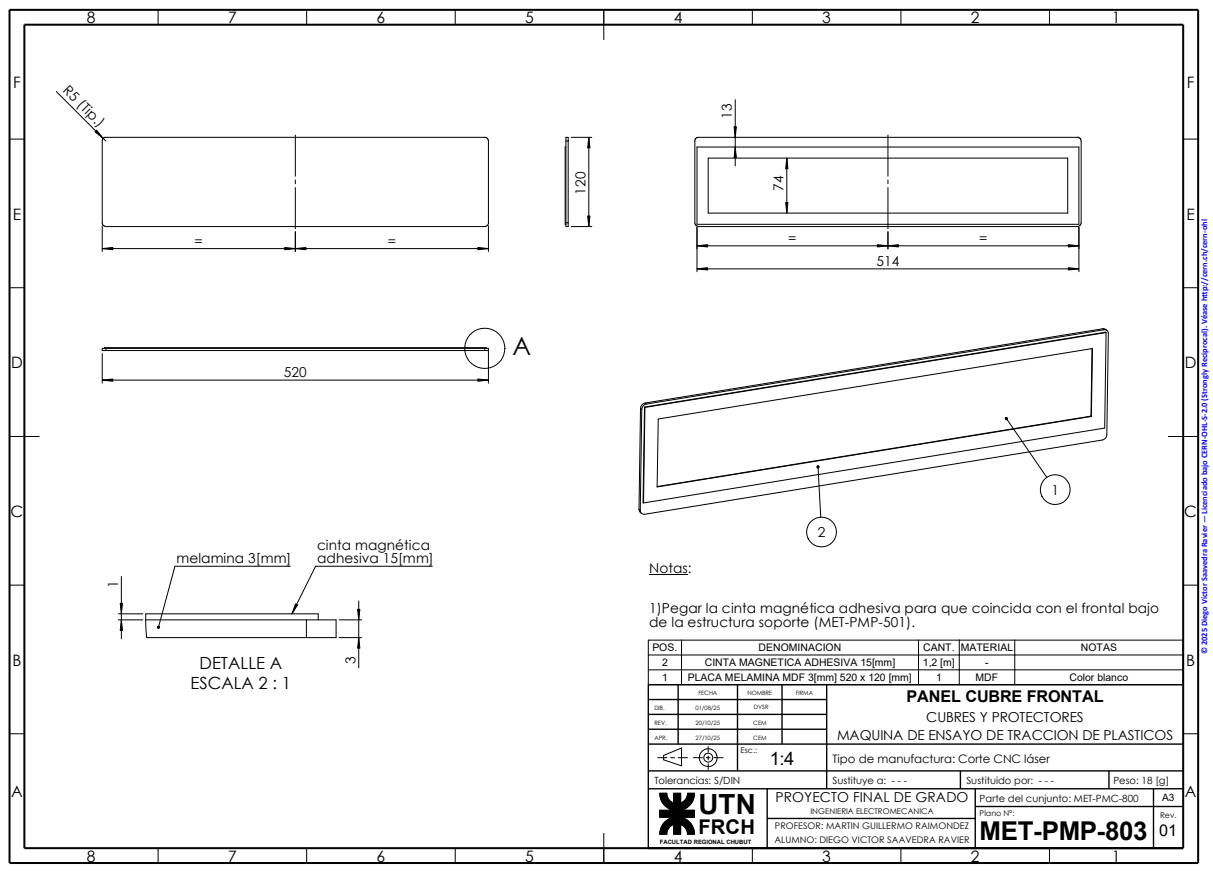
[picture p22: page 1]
UTN FRCH; DETALLE A ESCALA 2 : 1; melamina 3[mm]; cinta magnética adhesiva 15[mm] 3 1; R5 (Tip.); Notas:; © ²⁰²⁵ Diego Víctor Saavedra Ravier — Licenciado bajo CERN⁻OHL⁻S⁻2.0 ⁽Strongly Reciprocal). Véase hp://cern.ch/cern⁻ohl

1)Pegar la cinta magnética adhesiva para que coincida con el frontal bajo
de la estructura soporte (MET-PMP-501).

POS. | DENOMINACION | CANT. | MATERIAL | NOTAS
2 | CINTA MAGNETICA ADHESIVA 15[mm] | 1,2 [m] | -
1 | PLACA MELAMINA MDF 3[mm] 520 x 120 [mm] | 1 | MDF | Color blanco
FECHA | | FIRMA NOMBRE | PANEL CUBRE FRONTAL CUBRES Y PROTECTORES MAQUINA DE ENSAYO DE TRACCION DE PLASTICOS

DIB. | 01/08/25 | DVSR

REV. | 20/10/25 | CEM

APR. | 27/10/25 | CEM

Esc.: 1:4 | Tipo de manufactura: Corte CNC láser

Tolerancias: S/DIN | Sustituye a: - - - | Sustituido por: - - - | Peso: 18 [g]

FACULTAD REGIONAL CHUBUT | | | PROYECTO FINAL DE GRADO INGENIERIA ELECTROMECANICA | Parte del cunjunto: MET-PMC-800 | A3

Plano N°: MET-PMP-803 | Rev. 01

PROFESOR: MARTIN GUILLERMO RAIMONDEZ
ALUMNO: DIEGO VICTOR SAAVEDRA RAVIER

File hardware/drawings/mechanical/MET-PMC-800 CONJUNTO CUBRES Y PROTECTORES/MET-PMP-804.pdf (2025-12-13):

= | =

12 12

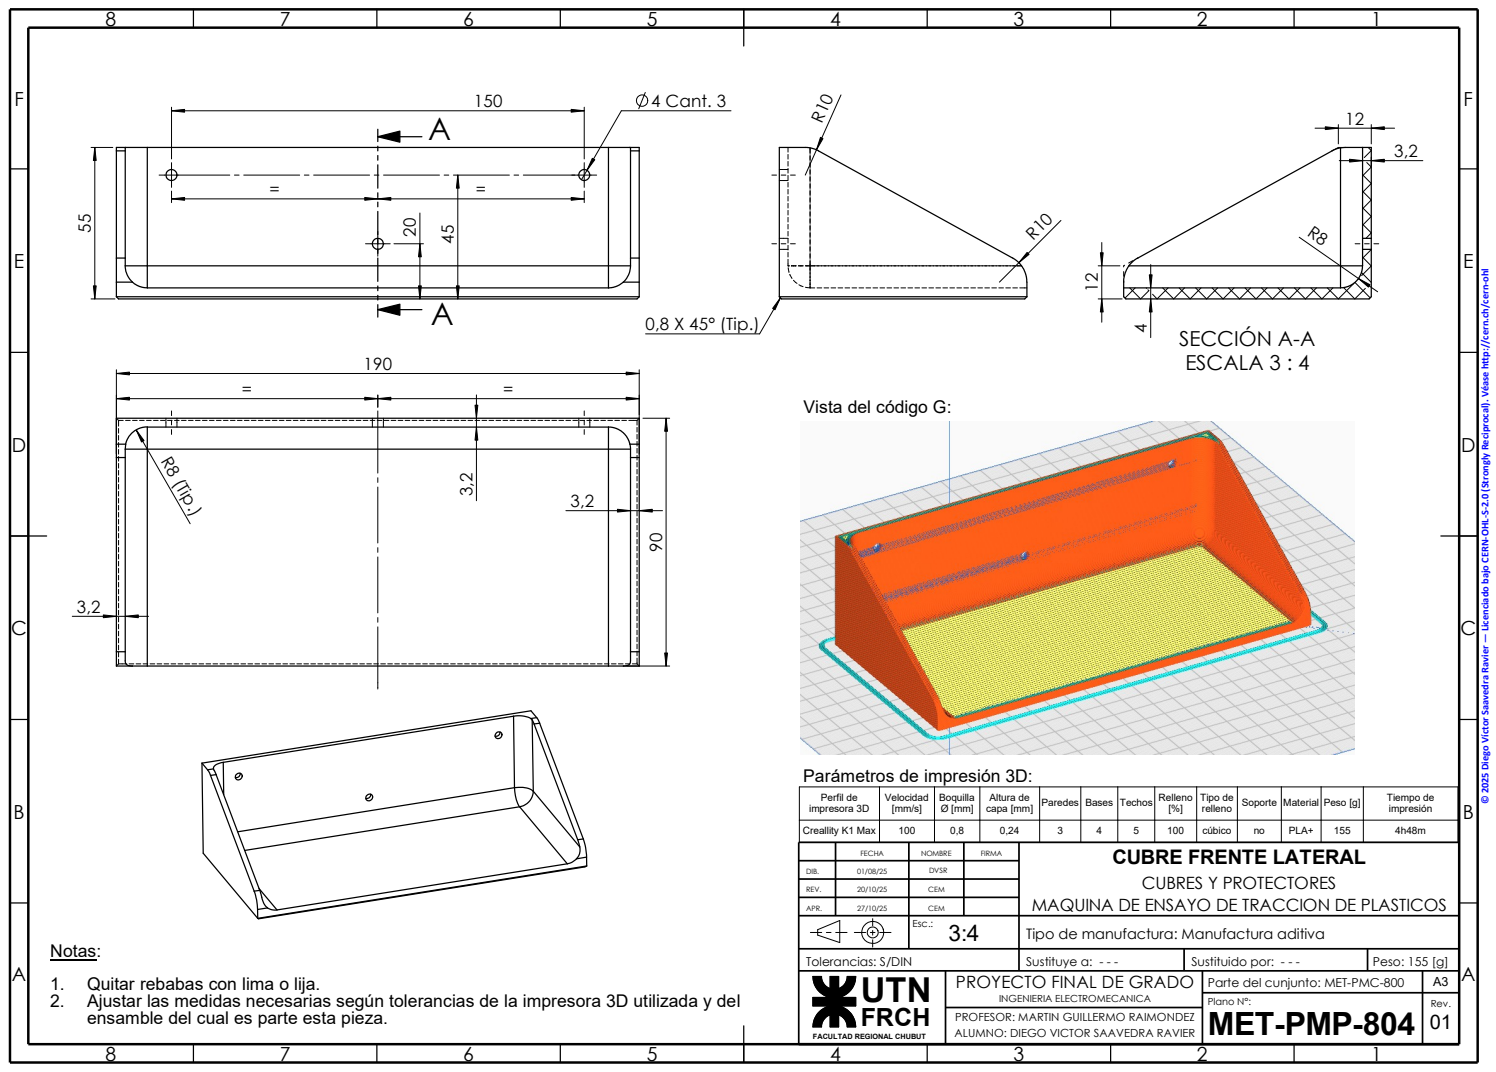
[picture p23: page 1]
UTN FRCH; 4 Cant. 3 55 A; 0,8 X 45° (Tip.); 3,2 R8 (Tip.); SECCIÓN A-A ESCALA 3 : 4

R8 © 2025 Diego Víctor Saavedra Ravier — Licenciado bajo CERN-OHL-S-2.0 (Strongly Reciprocal). Véase hp://cern.ch/cern-ohl

Vista del código G:

Parámetros de impresión 3D:

Perfil de impresora 3D | Velocidad [mm/s] | Boquilla Ø [mm] | capa [mm] Altura de | Paredes | Bases | Techos | Relleno [%] | Tipo de relleno | Soporte | Material | Peso [g] | Tiempo de impresión

Creallity K1 Max | 100 | 0,8 | 0,24 | 3 | 4 | 5 | 100 | cúbico | no | PLA+ | 155 | 4h48m
FECHA | | FIRMA NOMBRE | CUBRE FRENTE LATERAL CUBRES Y PROTECTORES MAQUINA DE ENSAYO DE TRACCION DE PLASTICOS

DIB. | 01/08/25 | DVSR

REV. | 20/10/25 | CEM

APR. | 27/10/25 | CEM

Esc.: 3:4 | Tipo de manufactura: Manufactura aditiva

Notas:
1. Quitar rebabas con lima o lija.
2. Ajustar las medidas necesarias según tolerancias de la impresora 3D utilizada y del
ensamble del cual es parte esta pieza.

Tolerancias: S/DIN | Sustituye a: - - - | Sustituido por: - - - | Peso: 155 [g]

FACULTAD REGIONAL CHUBUT | | | PROYECTO FINAL DE GRADO INGENIERIA ELECTROMECANICA | Parte del cunjunto: MET-PMC-800 | A3

Plano N°: MET-PMP-804 | Rev. 01

PROFESOR: MARTIN GUILLERMO RAIMONDEZ
ALUMNO: DIEGO VICTOR SAAVEDRA RAVIER

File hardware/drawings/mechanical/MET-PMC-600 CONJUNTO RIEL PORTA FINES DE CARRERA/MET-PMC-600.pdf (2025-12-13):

# riel 650

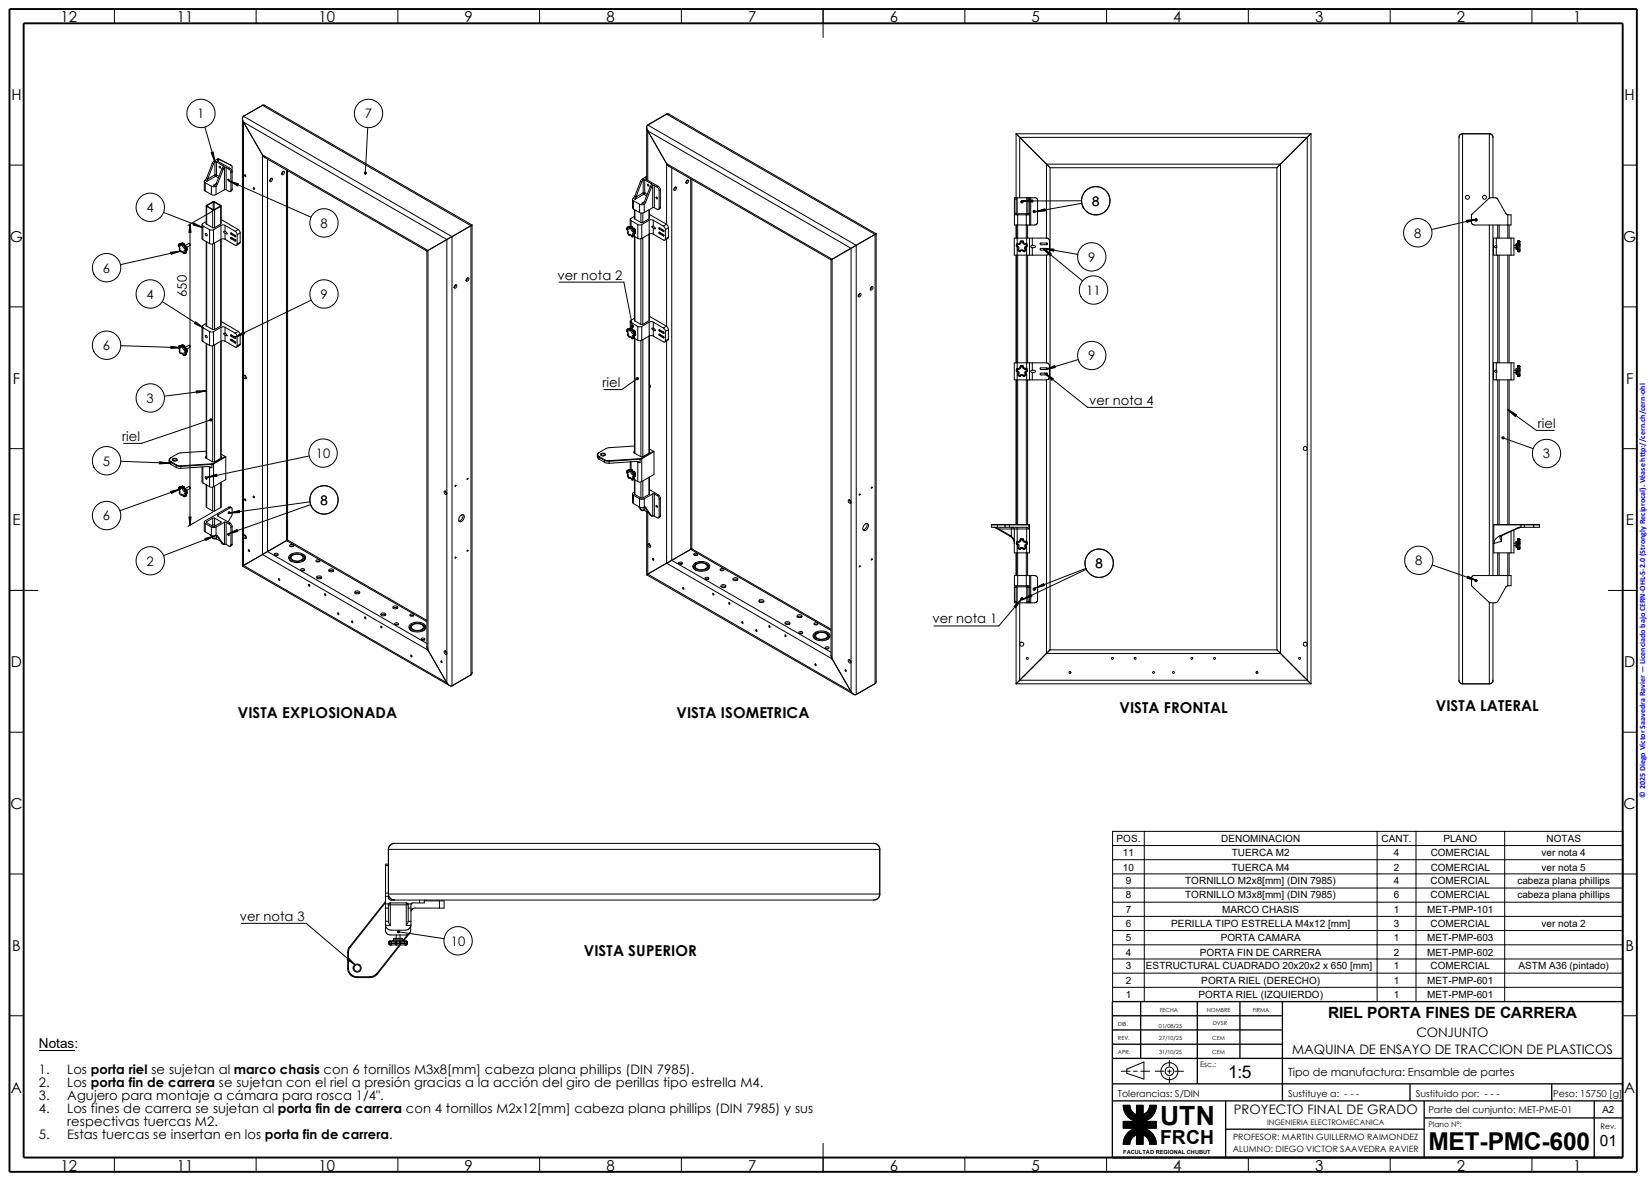
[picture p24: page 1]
UTN; MARCO CHASIS; MET-PMP-101; VISTA FRONTAL; VISTA SUPERIOR; VISTA LATERAL; riel; VISTA EXPLOSIONADA; VISTA ISOMETRICA; ver nota 2; ver nota 1; ver nota 4; ver nota 3

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

POS. | DENOMINACION | CANT. | PLANO | NOTAS
11 | TUERCA M2 | 4 | COMERCIAL | ver nota 4
10 | TUERCA M4 | 2 | COMERCIAL | ver nota 5
9 | TORNILLO M2x8[mm] (DIN 7985) | 4 | COMERCIAL | cabeza plana phillips
8 | TORNILLO M3x8[mm] (DIN 7985) | 6 | COMERCIAL | cabeza plana phillips

6 | PERILLA TIPO ESTRELLA M4x12 [mm] | 3 | COMERCIAL | ver nota 2
5 | PORTA CAMARA | 1 | MET-PMP-603
4 | PORTA FIN DE CARRERA | 2 | MET-PMP-602
3 | ESTRUCTURAL CUADRADO 20x20x2 x 650 [mm] | 1 | COMERCIAL | ASTM A36 (pintado)
2 | PORTA RIEL (DERECHO) | 1 | MET-PMP-601
1 | PORTA RIEL (IZQUIERDO) | 1 | MET-PMP-601

FECHA | NOMBRE | FIRMA | RIEL PORTA FINES DE CARRERA CONJUNTO MAQUINA DE ENSAYO DE TRACCION DE PLASTICOS

DIB. | 01/08/25 | DVSR

Notas:
1. Los porta riel se sujetan al marco chasis con 6 tornillos M3x8[mm] cabeza plana phillips (DIN 7985).
2. Los porta fin de carrera se sujetan con el riel a presión gracias a la acción del giro de perillas tipo estrella M4.
3. Agujero para montaje a cámara para rosca 1/4".
4. Los fines de carrera se sujetan al porta fin de carrera con 4 tornillos M2x12[mm] cabeza plana phillips (DIN 7985) y sus
respectivas tuercas M2.
5. Estas tuercas se insertan en los porta fin de carrera.

REV. | 27/10/25 | CEM

APR. | 31/10/25 | CEM

Esc.: 1:5 | Tipo de manufactura: Ensamble de partes

Tolerancias: S/DIN | Sustituye a: - - - | Sustituido por: - - - | Peso: 15750 [g]

PROYECTO FINAL DE GRADO INGENIERIA ELECTROMECANICA | Parte del cunjunto: MET-PME-01 | A2

FRCH FACULTAD REGIONAL CHUBUT

Plano N°: MET-PMC-600 | Rev. 01

PROFESOR: MARTIN GUILLERMO RAIMONDEZ
ALUMNO: DIEGO VICTOR SAAVEDRA RAVIER

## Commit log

2025-12-13 Add files via upload
    Diapositiva utilizada para la defensa de mi Proyecto Final de Grado, respecto al desarrollo de esta máquina.
    En cuanto a la duración de la presentación, el objetivo fue hacerlo en menos de 45min.
2025-12-13 Rename tensile testing machine astm d638.pdf to tensile-testing-machine-astm-d638_PFG_Diego-Saavedra-Ravier_2025.pdf.pdf
    cambio de nombre
2025-12-13 Add files via upload
    Proyecto Final de Grado de Ingeniería Electromecánica.
    Diseño y cálculo de una máquina de ensayo de tracción para plásticos según norma ASTM D638.
    Incluye fundamento teórico, selección normativa, diseño mecánico, análisis FEA,
    sistema extensométrico (DIC), electrónica de control, planos y documentación completa.
    Autor: Diego Víctor Saavedra Ravier (2025).
2025-12-13 Rename hardware/cad/Probeta astmD638_Type I.SLDPRT to hardware/cad/solidworks/Probeta astmD638_Type I.SLDPRT
    [Probeta astmD638_Type I.SLDPRT]
2025-12-13 Rename hardware/cad/Probeta astmD638_Type II.SLDPRT to hardware/cad/solidworks/Probeta astmD638_Type II.SLDPRT
    [Probeta astmD638_Type II.SLDPRT]
2025-12-13 Rename hardware/cad/Probeta astmD638_Type III.SLDPRT to hardware/cad/solidworks/Probeta astmD638_Type III.SLDPRT
    [Probeta astmD638_Type III.SLDPRT]
2025-12-13 Rename hardware/cad/Probeta astmD638_Type IV.SLDPRT to hardware/cad/solidworks/Probeta astmD638_Type IV.SLDPRT
    [Probeta astmD638_Type IV.SLDPRT]
2025-12-13 Rename hardware/cad/Probeta astmD638_Type V.SLDPRT to hardware/cad/solidworks/Probeta astmD638_Type V.SLDPRT
    [Probeta astmD638_Type V.SLDPRT]

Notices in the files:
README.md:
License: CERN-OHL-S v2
